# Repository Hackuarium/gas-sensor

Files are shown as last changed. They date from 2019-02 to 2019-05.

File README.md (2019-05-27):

# gas-sensor

<p align="center">
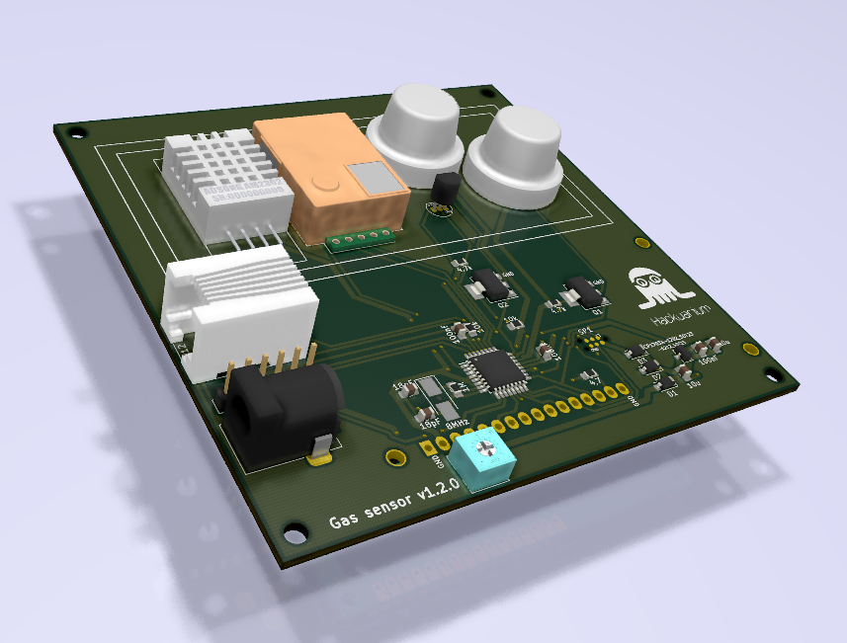
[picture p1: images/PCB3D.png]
  
</p>

The goal is to create a box allowing the determination of the gas composition of a bioreactor. The sensor that will be available are: CO2 (MH-Z19), H2 (MQ-8) and methane (MQ-4) as well as temperature (DS18B20) and humidity (DHT-22).

The board will be compatible with arduino Lilapad Pro using a dedicated PCB.

Need to compensate for humidity and temperature ???

- https://forum.arduino.cc/index.php?topic=433045.0

## Cloning the project

This project uses SUBMODULES

In order to clone use:

`git clone --recurse-submodules https://github.com/hackuarium/gas-sensor`

To update the submodules

`git submodule update --recursive --remote`

## Sensors

| name_pin | function    | model   |                             | Arduino library                                |
| -------- | ----------- | ------- | --------------------------- | ---------------------------------------------- |
| CH4      | CH4         | MQ-4    |                             |                                                |
| H2       | H2          | MQ-8    |                             |                                                |
| CO2      | CO2         | MH-Z19  | 3.3v (for RX / TX) + 5v!!!! | https://github.com/crisap94/MHZ19              |
| TEMP     | temperature | DS18B20 |                             |                                                |
| HUM      | humidity    | DHT-22  |                             | https://github.com/adafruit/DHT-sensor-library |

Gaz sensor: http://www.china-total.com/Product/meter/gas-sensor/Gas-sensor.htm

Gaz sensor on sparkfun:
https://www.sparkfun.com/products/8891
https://www.sparkfun.com/products/9404

Gaz sensor on mysensors: https://www.mysensors.org/build/gas

Drying the air / pumping
Particulate or Coalescing Filters
http://www.pneumaticplus.com/pneumaticplus-saf4000-series-particulate-air-filter-1-2-npt-with-bracket/
https://www.aliexpress.com/item/15L-M-12V-dc-electric-diaphragm-brush-small-air-compressor-pump/1790013118.html

Fans

https://www.pelonistechnologies.com/micro-fans

Pneumatic
https://www.alibaba.com/product-detail/A102-China-sup

## Pinout

| n° Arduino | port | pin      |                  |     |
| ---------- | ---- | -------- | ---------------- | --- |
| A0         | PC0  | A0       | H2               |     |
| A1         | PC1  | A1       | H2_ON            |     |
| A2         | PC2  | A2       | CO2_RX           |     |
| A3         | PC3  | A3       | CO2_TX           |     |
| A4         | PC4  | SDA      | Slave I2C        |     |
| A5         | PC5  | SCL      | Slave I2C        |     |
| A6         | ADC6 | A6       | CH4              |     |
| A7         | ADC7 | A7       | CH4_ON           |     |
| 0          | PD0  | RX       | FTDI             |     |
| 1          | PD1  | TX       | FTDI             |     |
| 2          | PD2  | D2       | /                |     |
| 3          | PD3  | D3       | PWM_MH-Z19       | PWM |
| 4          | PD4  | D4       | TEMPERATURE      |     |
| 5          | PD5  | D5       | HUMIDITY         | PWM |
| 6          | PD6  | D6       | LCD RS           | PWM |
| 7          | PD7  | D7       | /                |     |
| 8          | PB0  | D8       | LCD E            |     |
| 9          | PB1  | D9       | LCD LED          | PWM |
| 10         | PB2  | D10      | LCD1             | PWM |
| 11         | PB3  | MOSI D11 | LCD2             | PWM | mh |
| 12         | PB4  | MISO D12 | LCD3             |     |
| 13         | PB5  | SCK D13  | LCD4             |     |

n.b: Two pins (PD2 and PD7) are free and could be used to add a fourth sensor.

## Power supply

- plug for 5V
- MCP1703-33 for µC power supply

## Schematic
Here is the schematic of the main components of the project:

ATMega328P:
<p align="center">
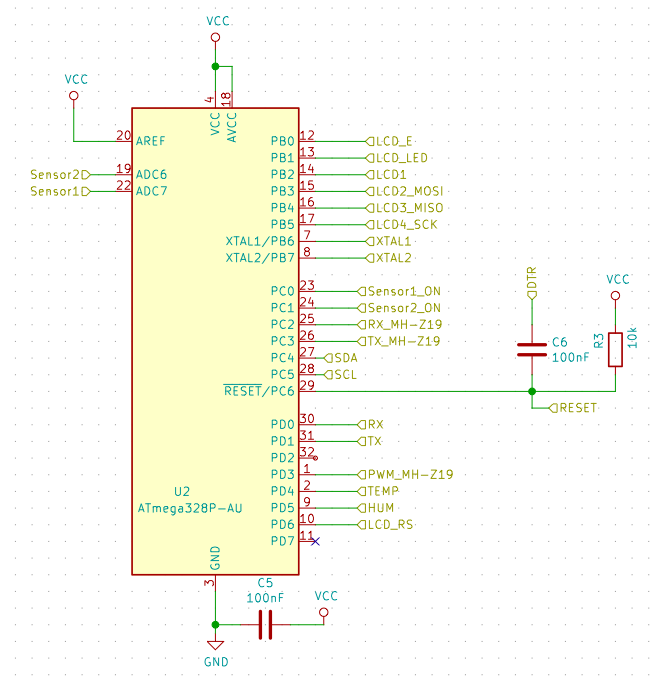
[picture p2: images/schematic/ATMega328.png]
  
</p>
Sensors:
<p align="center">
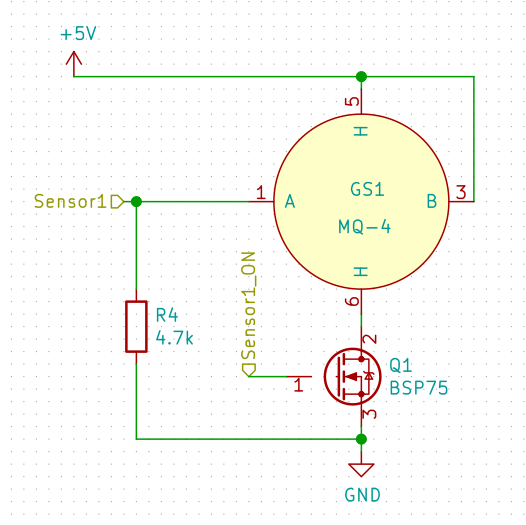
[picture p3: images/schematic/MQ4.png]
  
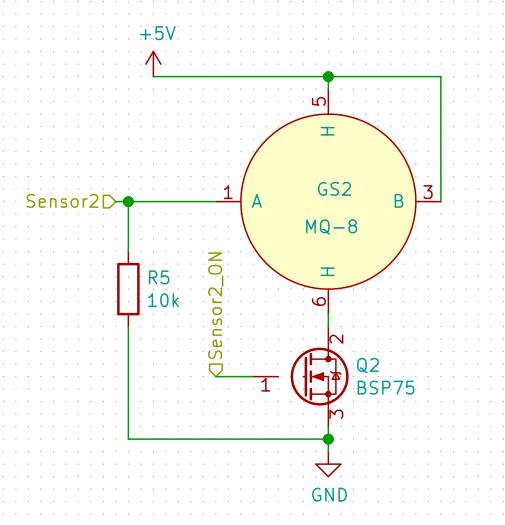
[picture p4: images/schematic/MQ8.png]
  
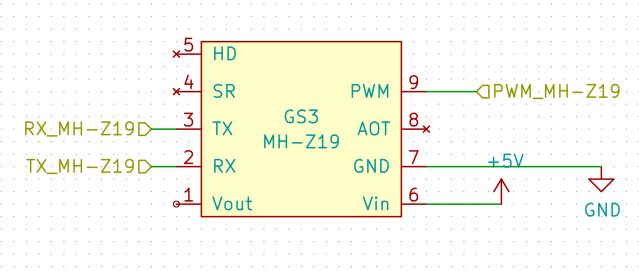
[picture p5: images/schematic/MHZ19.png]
  
</p>
<p align="center">
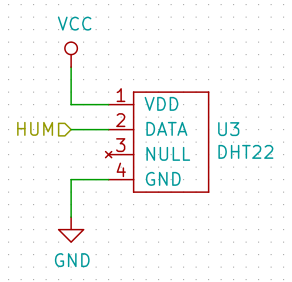
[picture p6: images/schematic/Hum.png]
  
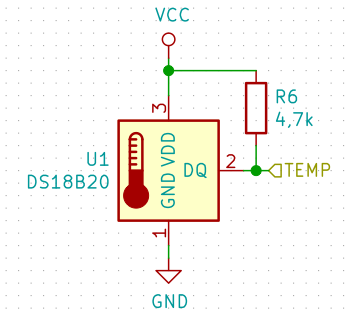
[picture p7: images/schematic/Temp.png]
  
</p>
Others (LCD, crystal and voltage regulator):
<p align="center">
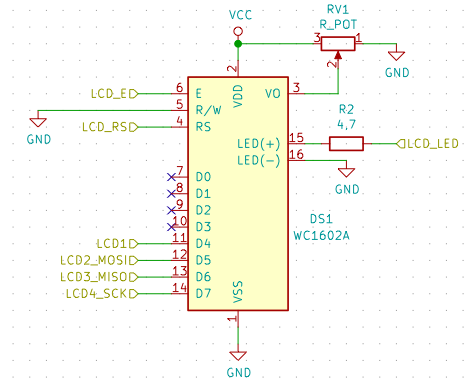
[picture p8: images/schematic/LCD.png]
  
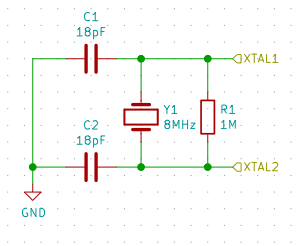
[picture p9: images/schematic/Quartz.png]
  
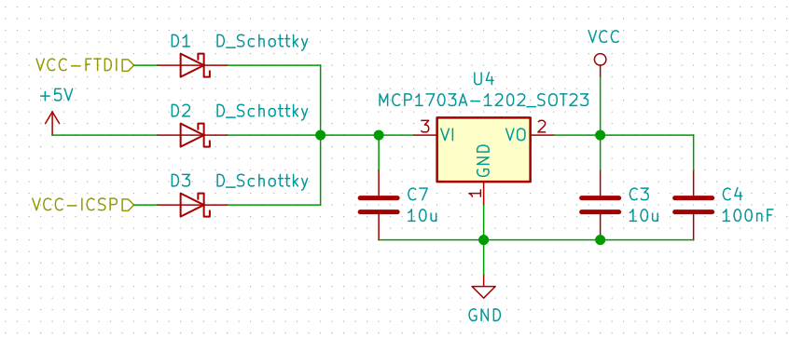
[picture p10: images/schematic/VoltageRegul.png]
  
</p>

## List of components
| Type           | Value | Quantity | Footprint                   |
|----------------|-------|----------|-----------------------------|
| Resistor       | 1M    | 1        | 0805 Handsolder             |
| Resistor       | 10k   | 2        | 0805 Handsolder             |
| Resistor       | 4.7k  | 2        | 0805 Handsolder             |
| Resistor       | 4.7   | 1        | 0805 Handsolder             |
| Potentiometer  |       | 1        | TRIM_3362R-1-222            |
| Capacitor      | 10µF  | 2        | 0805 Handsolder             |
| Capacitor      | 100nF | 3        | 0805 Handsolder             |
| Capacitor      | 18pF  | 2        | 0805 Handsolder             |
| Diode Shottky  |       | 3        | D_SOD-123                   |
| BSP75          |       | 2        | SOT-223-3_TabPin3           |
| Crystal        | 8Mhz  | 1        | Crystal_SMD_5032 Handsolder |
| MCP-1703A      |       | 1        | SOT-23                      |
| ATMega328P-AU  |       | 1        | TQFP-32_7x7mm_P0.8mm        |
| 5V power source|       | 1        | BarrelJack_Horizontal       |
| RJ12           |       | 1        | RJ12_Amphenol_54601         |
| LCD Screen     |       | 1        | WC1602A                     |
| MHZ-19 (CO2)   |       | 1        | footprints: MHZ-19          |
| MQ-4 (CH4)     |       | 1        | footprints: MQ-4            |
| MQ-8 (H2)      |       | 1        | footprints: MQ-8            |
| DHT22 (Hum)    |       | 1        | footprints: DHT-22_HOR      |
| DS18B20 (Temp) |       | 1        | TO-92_Inline                |

## Inspiration for PCB

* https://github.com/Hackuarium/esp-12e/tree/master/kicad

  - ICSP - TAG connect - take care of pin mapping !
  - RJ12 - 6P6C
  - FTDI232
  - LCD: WC1602A

## Get inspired from scale board

- https://github.com/Hackuarium/beemos/tree/master/scale-i2c/eagle
- https://github.com/Hackuarium/esp-12e/tree/master/kicad/libs

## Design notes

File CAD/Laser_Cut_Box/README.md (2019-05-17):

The case is designed to be cut in a 3mm-wide material, using a CNC (Computer Numerical Control) router, mounted with a 1,2mm-drill bit. Plexiglas has been used and shows relative good performances. Before cutting, drilling parameters must be set as follow:
* the outer contour of each piece must be set at "outside cut".
* all the other "holes" must be set at "inside cut"

Here are some pictures of the mounted box, without the hermetic "aquarium" in the middle.
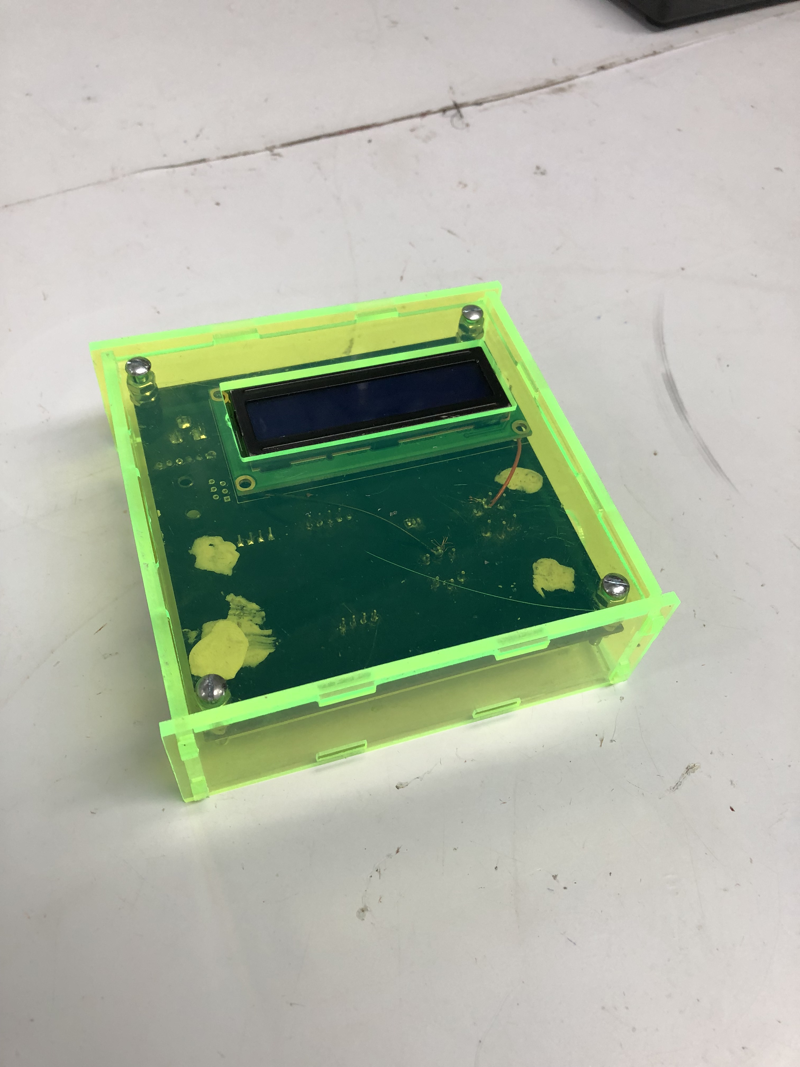
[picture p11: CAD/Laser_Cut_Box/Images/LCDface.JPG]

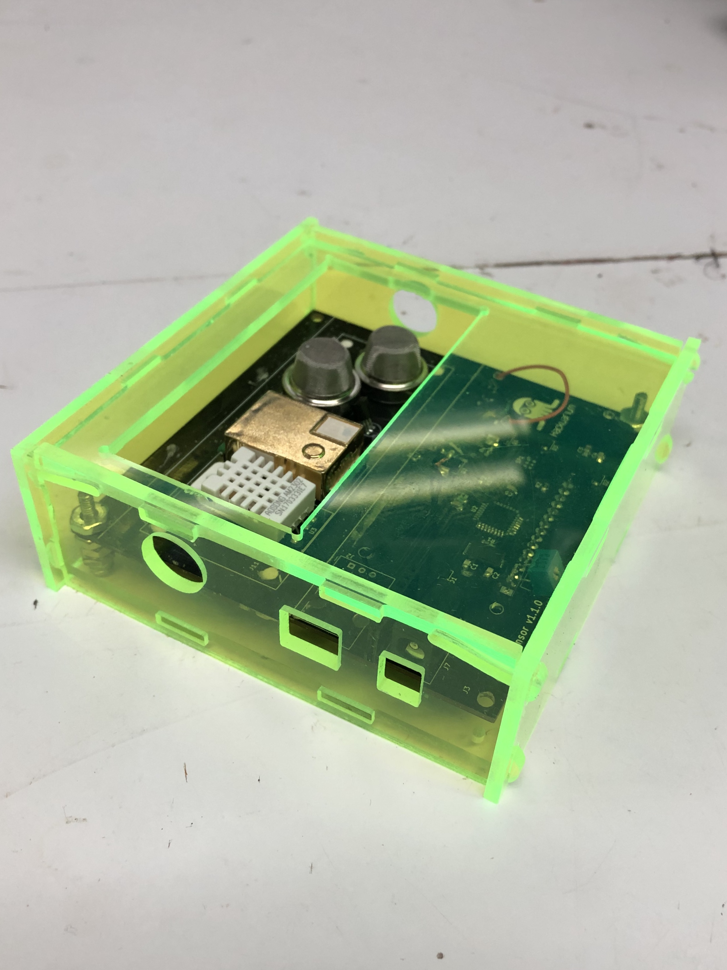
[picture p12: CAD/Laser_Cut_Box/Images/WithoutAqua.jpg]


When all the pieces are correctly obtained, one can easily assemble the case proceeding as follow:
* Glue the different parts of the aquarium together. Acrylic resine Veracril© has been used.
* Then, glue the plexiglas box directly on the chip. Assure that it is well hermetic. Silicon gun was used for ensuring absence of leaks.
* Screw the chip with the "bottom" part (the one having a round hole in each corner) using M3 screws. One can use bolts for instance to adjsut the height, as seen in the picture:
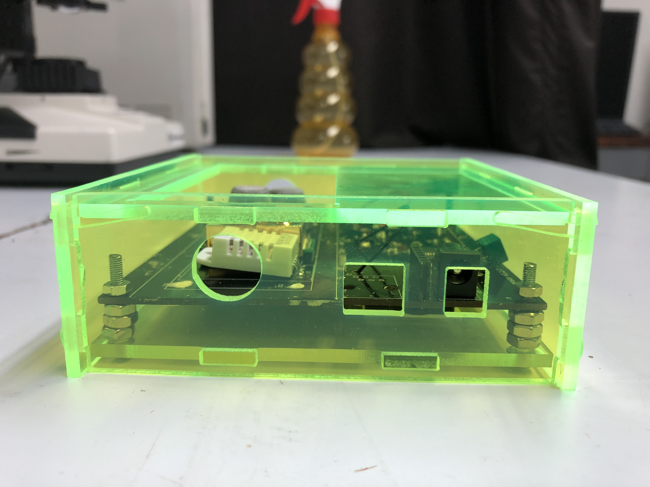
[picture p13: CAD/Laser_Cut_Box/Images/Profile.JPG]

* Place both the "left" and "right" part (the ones with the linear split and the hole for the gas pipe) on each side of the chip.
* Slide the "top" part above it and between the "left" and "right" parts.
* Clip the "up" and "down" parts to the case.

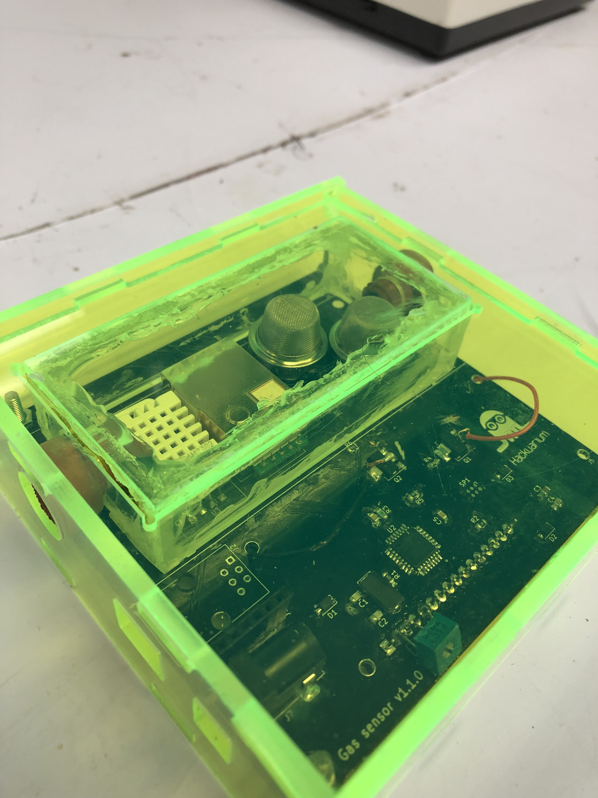
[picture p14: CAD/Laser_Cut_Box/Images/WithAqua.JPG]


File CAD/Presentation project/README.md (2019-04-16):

This folder contains temporary designs that were solely used for a presentation showing current progress on the project.

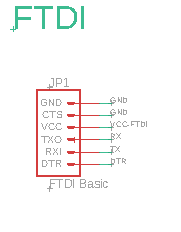
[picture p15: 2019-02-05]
images/ftdi.png

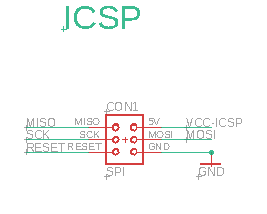
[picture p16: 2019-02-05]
images/icsp.png

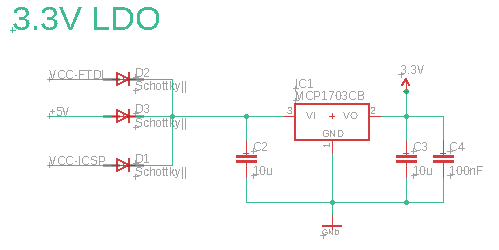
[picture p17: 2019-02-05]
images/ldo.png

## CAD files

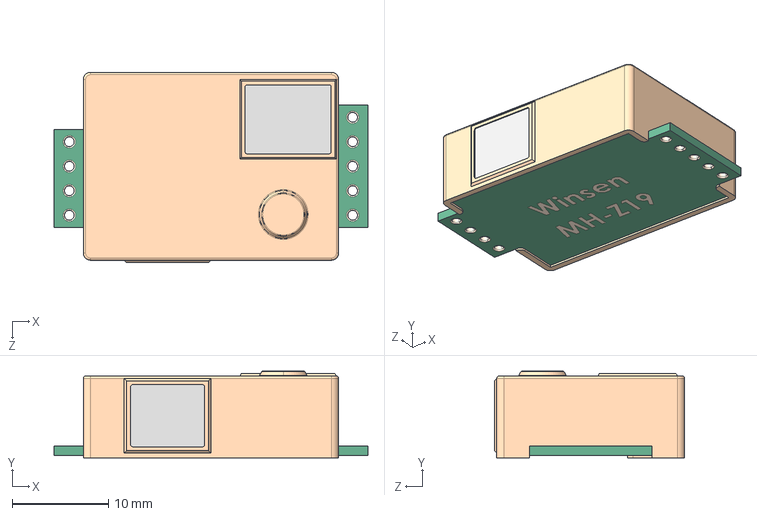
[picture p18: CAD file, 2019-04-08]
kicad/shapes3D/MH-Z19.STEP
32.6 x 9.00 x 19.7 mm

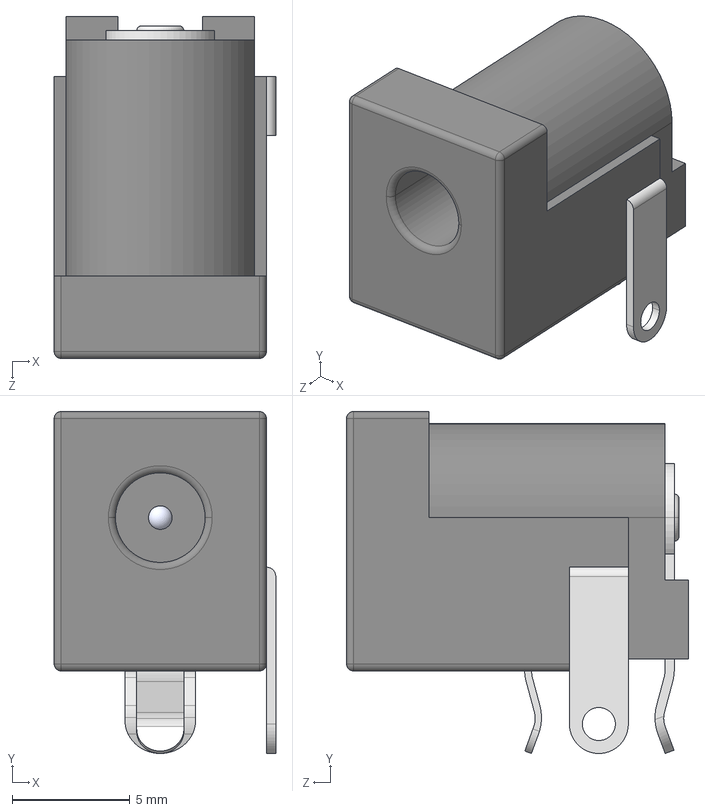
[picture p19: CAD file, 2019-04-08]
kicad/shapes3D/CUI_PJ-017C.step
9.40 x 14.5 x 14.5 mm

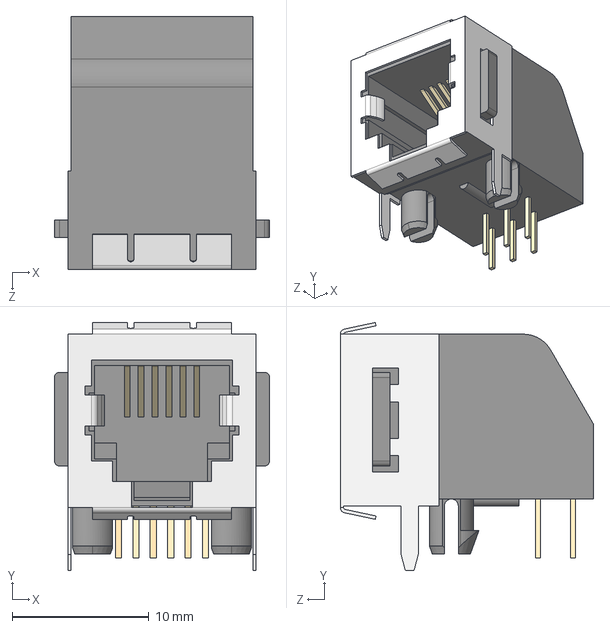
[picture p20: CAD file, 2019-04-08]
kicad/shapes3D/rj12_90deg.step
15.7 x 18.1 x 18.5 mm

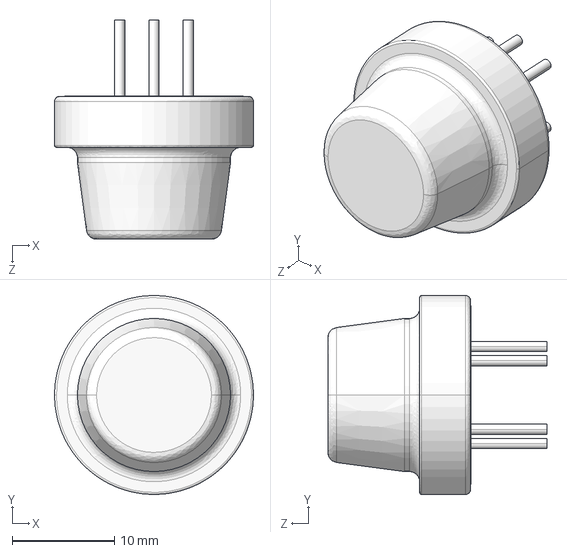
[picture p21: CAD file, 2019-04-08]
kicad/shapes3D/MQ135.STEP
19.5 x 19.5 x 21.5 mm

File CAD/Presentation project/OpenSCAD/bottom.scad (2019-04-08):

$fn = 50;

bottom();

//The bottom part (with LCD screen)
module bottom(bLength = 106, bWidth = 106, bHeight = 11, bWalls = 3, DiamScrew = 3){
    difference(){
        cube([bLength, bWidth, bHeight], center = true);
        translate([0,0,1.501]){
            cube([bLength-2*bWalls, bWidth-2*bWalls, bHeight-bWalls], center = true);
        }
        
        //hole for the screen
        screen_L = 70.7;
        screen_W = 23.8;
        X_POS = screen_L/2+4.2;
        Y_POS = screen_W/2+12.85;
        translate([-bLength/2+bWalls+X_POS,bWidth/2-bWalls-Y_POS,-3]) cube([screen_L, screen_W, 2*bWalls],center = true);
        //holes for the screw
        OFFSET = 3.4;
        translate([(bLength-2*bWalls)/2-OFFSET,(bWidth-2*bWalls)/2-OFFSET,-bWalls])Screwhole(DiamScrew, bWalls);
        translate([-(bLength-2*bWalls)/2+OFFSET,(bWidth-2*bWalls)/2-OFFSET,-bWalls])Screwhole(DiamScrew, bWalls);
        translate([-(bLength-2*bWalls)/2+OFFSET,-(bWidth-2*bWalls)/2+OFFSET,-bWalls])Screwhole(DiamScrew, bWalls);
        translate([(bLength-2*bWalls)/2-OFFSET,-(bWidth-2*bWalls)/2+OFFSET,-bWalls])Screwhole(DiamScrew, bWalls);
    }
        
}

module Screwhole(DiamScrew = 3, bWalls = 3){
    cylinder(d=DiamScrew, h=2*bWalls, center = true);
}

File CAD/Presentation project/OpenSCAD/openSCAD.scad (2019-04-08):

$fn = 50;

use <top.scad>
use <bottom.scad>
use <plexiBox.scad>
use <pcb.scad>

openSCAD();

//Dimensions for top box:
tLength = 106;
tWidth = 106;
tHeight = 23;
tWalls = 3;

//Dimensions for bottom box
bLength = 106;
bWidth = 106;
bHeight = 11;
bWalls = 3;

//Dimensions for plexibox
pLength = 100;
pWidth = 46.35;
pHeight = 23;
pWalls = 6;

//Dimensions for PCB
pcbL = 100;
pcbW = 100;
pcbH = 1;

//Dimensions for screw
DiamScrew = 3;

//Dimensions for pipe
radPipe = 6;

module openSCAD(){
    top(tLength, tWidth, tHeight, tWalls, DiamScrew, pLength, pWidth, radPipe);
    translate([0,(tWidth-2*tWalls-pWidth)/2-7.15,0]){
        color("LightCyan",0.5) plexiBox(pLength, pWidth, pHeight, pWalls, radPipe, DiamScrew);
    }
    rotate([0,0,180]){
        translate([0,0,-18])bottom(bLength, bWidth, bHeight, bWalls, DiamScrew);
    }
    translate([0,0,-12]){
        //pcb(pcbL, pcbW, pcbH);
    }

}

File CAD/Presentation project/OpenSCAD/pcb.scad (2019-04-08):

$fn = 50;

pcb();

module pcb(pcbL = 100, pcbW = 100, pcbH = 1){
    color("pink") cube([pcbL,pcbW, pcbH],center = true);
}

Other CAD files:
CAD/Laser_Cut_Box/Test_Pro_Cutting.FCStd
CAD/Laser_Cut_Box/Final_Cut_Box.FCStd
CAD/Presentation project/OpenSCAD/Pipehole.scad
CAD/Presentation project/OpenSCAD/Screwhole.scad
CAD/Presentation project/OpenSCAD/plexiBox.scad
CAD/Presentation project/OpenSCAD/top.scad

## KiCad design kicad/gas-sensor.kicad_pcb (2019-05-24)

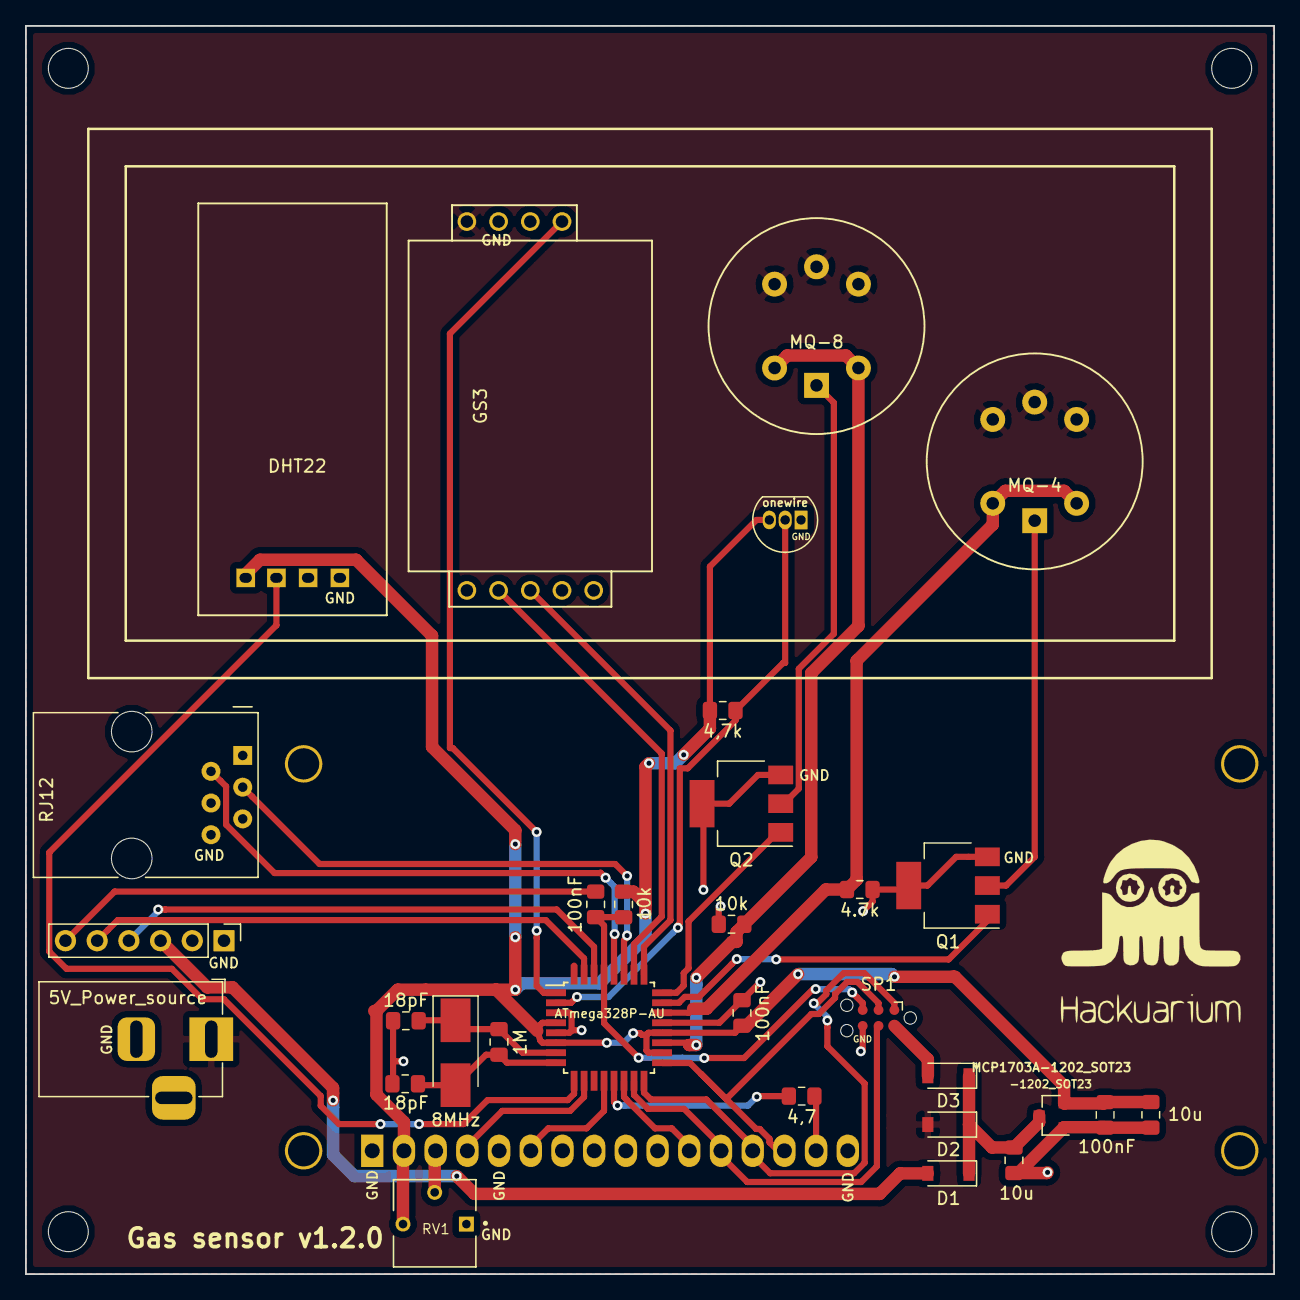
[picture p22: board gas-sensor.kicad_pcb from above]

Board: 2 copper layers, 100.0 x 100.0 mm, 37 parts (1 on the bottom side), 34 nets.

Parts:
C1, C2: 18pF; C_0805_2012Metric_Pad1.15x1.40mm_HandSolder
C3, C7: 10u; C_0805_2012Metric_Pad1.15x1.40mm_HandSolder
C4, C5, C6: 100nF; C_0805_2012Metric_Pad1.15x1.40mm_HandSolder
D1, D2, D3: D_Schottky; D_SOD-123
DS1: WC1602A
G1: LOGO; hackuarium
GS1: MQ-4
GS2: MQ-8
GS3: MH-Z19
J1: Conn FT232RL; PinHeader_1x06_P2.54mm_Vertical
J2: RJ12; RJ12_Amphenol_54601
J3, J4, J5, J6: hole; MountingHole_3.2mm_M3
J7: 5V_Power_source; BarrelJack_Horizontal
Q1, Q2: BSP75; SOT-223-3_TabPin3
R1: 1M; R_0805_2012Metric_Pad1.15x1.40mm_HandSolder
R2: 4,7; R_0805_2012Metric_Pad1.15x1.40mm_HandSolder
R3, R5: 10k; R_0805_2012Metric_Pad1.15x1.40mm_HandSolder
R4: 4.7k; R_0805_2012Metric_Pad1.15x1.40mm_HandSolder
R6: 4,7k; R_0805_2012Metric_Pad1.15x1.40mm_HandSolder
RV1: R_POT; TRIM_3362R-1-222
SP1: ICSP; Tag-Connect_TC2030-IDC-NL_2x03_P1.27mm_Vertical
U1: DS18B20; TO-92_Inline
U2: ATmega328P-AU; TQFP-32_7x7mm_P0.8mm
U3: DHT22; DHT22_HOR
U4: MCP1703A-1202_SOT23; SOT-23
Y1: 8MHz; Crystal_SMD_5032-2Pin_5.0x3.2mm_HandSoldering

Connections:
+5V: D2.2, GS1.3, GS1.4, GS1.5, GS2.3, GS2.4, GS2.5, GS3.6, J7.1
/DTR: C6.1, J1.6
/HUM: U2.9, U3.2
/LCD1: DS1.11, U2.14
/LCD2_MOSI: DS1.12, SP1.4, U2.15
/LCD3_MISO: DS1.13, SP1.1, U2.16
/LCD4_SCK: DS1.14, SP1.3, U2.17
/LCD_E: DS1.6, U2.12
/LCD_LED: R2.1, U2.13
/LCD_RS: DS1.4, U2.10
/PWM_MH-Z19: GS3.9, U2.1
/RESET: C6.2, R3.2, SP1.5, U2.29
/RX: J1.4, U2.30
/RX_MH-Z19: GS3.3, U2.25
/SCL: J2.2, U2.28
/SDA: J2.3, U2.27
/Sensor1: GS1.1, GS1.2, R4.1, U2.22
/Sensor1_ON: Q1.1, U2.23
/Sensor2: GS2.1, GS2.2, R5.1, U2.19
/Sensor2_ON: Q2.1, U2.24
/TEMP: R6.2, U1.2, U2.2
/TX: J1.5, U2.31
/TX_MH-Z19: GS3.2, U2.26
/VCC-FTDI: D1.2, J1.3
/VCC-ICSP: D3.2, SP1.2
/XTAL1: C1.1, R1.1, U2.7, Y1.1
/XTAL2: C2.1, R1.2, U2.8, Y1.2
GND: C1.2, C2.2, C3.2, C4.2, C5.2, C7.2, DS1.1, DS1.5, DS1.16, GS3.7, J1.1, J2.4, J2.6, J7.2, Q1.3, Q2.3, R4.2, R5.2, RV1.1, SP1.6, U1.1, U2.3, U2.5, U2.21, U3.4, U4.1
unnamed: C7.1, D1.1, D2.1, D3.1, U4.3
unnamed: DS1.3, RV1.2
unnamed: DS1.15, R2.2
unnamed: GS1.6, Q1.2
unnamed: GS2.6, Q2.2
VCC: C3.1, C4.1, C5.1, DS1.2, R3.1, R6.1, RV1.3, U1.3, U2.4, U2.6, U2.18, U2.20, U3.1, U4.2

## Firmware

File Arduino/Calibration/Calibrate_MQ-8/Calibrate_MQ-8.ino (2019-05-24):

/*Calibration of the sensor MQ-8, and allow to test it afterwards*/
// inspiration: http://sandboxelectronics.com/?p=196

/************************Hardware Related Macros************************************/
#define         H2_PIN                       A6     //define which analog input channel you are going to use
#define         H2_ON_PIN                    A1     // set on HIGH to turn the sensor on
#define         RL_VALUE                     10     //define the load resistance on the board, in kilo ohms
#define         RO_CLEAN_AIR_FACTOR          70     //RO_CLEAR_AIR_FACTOR=(Sensor resistance in clean air)/RO,
                                                     //derived from the chart in datasheet
 
/***********************Software Related Macros************************************/
#define         CALIBRATION_SAMPLE_TIMES     300    //define how many samples you are going to take in the calibration phase
#define         CALIBRATION_SAMPLE_INTERVAL  500    //define the time interal(in milisecond) between each samples in the
                                                    //cablibration phase
#define         READ_SAMPLE_INTERVAL         100    //define how many samples you are going to take in normal operation
#define         READ_SAMPLE_TIMES            20     //define the time interal(in milisecond) between each samples in 
                                                    //normal operation
                                                     
/*****************************Globals***********************************************/
float           H2Curve[2]  =  {-1.44, 4.25};       //Line representing the relationship between the log of the concentration
                                                    //of H2 in ppm (x) and the log of the ratio of resistances Rs/Ro (y)
                                                    //{a, b}, log(y) = a*log(x) + b;
                                                    //The two points chosen: {200, 8.5} and {10000, 0.403}  
 
float           Ro           =  14.01;              //Last Ro found with this programm, 14.01 kOhm. TOCHANGE at evry new calibration
bool            Calib_bool   =  true;              //Set to True if calibration is needed (fresh air condition expected)


void setup() {
  Serial.begin(9600);                               //UART setup, baudrate = 9600bps
  pinMode(H2_ON_PIN, OUTPUT);
  digitalWrite(H2_ON_PIN, HIGH);
  if(Calib_bool){
    Serial.print("Calibrating...\n");                
    Ro = MQCalibration();                           //Calibrating the sensor. Please make sure the sensor is in clean air
                                                    //when you perform the calibration 
    Serial.println("Calibration is done: Ro = " + String(Ro) + " kOhm");
  }                                                                     

}

//Average the value read from the analog pin, and if in the range, compute the ppm from it
void loop(){
  int i;
  float sensorValue=0;
  float analog;
 
  while(true){
    for (i = 0; i < READ_SAMPLE_TIMES; i++){
      analog = analogRead(H2_PIN);
      Serial.println("analog = " + String(analog) + " / "); 
      sensorValue += analog;
      delay(READ_SAMPLE_INTERVAL);
    }
    
    sensorValue = sensorValue/READ_SAMPLE_TIMES;
    if(sensorValue <= 1){
      Serial.println("Not enough H2 (" + String(sensorValue) + ")");
    }
    else if(sensorValue >= 1023){
      Serial.println("Too much H2 (" + String(sensorValue) + ")");
    }
    else{
    Serial.print("Value = " + String(sensorValue) + " / ");
    getH2(sensorValue);
    }
    sensorValue = 0;
    delay(1000);
  }
}

/***************************** MQCalibration ****************************************
Input:   mq_pin - analog channel
Output:  Ro of the sensor
Remarks: This function assumes that the sensor is in clean air. It use  
         MQResistanceCalculation to calculates the sensor resistance in clean air 
         and then divides it with RO_CLEAN_AIR_FACTOR.
************************************************************************************/ 
float MQCalibration() {
  int i;
  float val=0;
  delay(5000);
  for (i=0;i<CALIBRATION_SAMPLE_TIMES;i++) {            //take multiple samples
    int pin_value = analogRead(H2_PIN);
    if(i%5 == 0){
      Serial.println("sample n°:"+ String(i) + ", pin value = " + String(pin_value));
    }
    val += MQResistanceCalculation(pin_value);
    delay(CALIBRATION_SAMPLE_INTERVAL);
  }
  val = val/CALIBRATION_SAMPLE_TIMES;                   //calculate the average value
 
  val = val/RO_CLEAN_AIR_FACTOR;                        //divided by RO_CLEAN_AIR_FACTOR yields the Ro 
                                                       //according to the chart in the datasheet 
                                                         
  return val; 
}

/*****************************  getH2 *********************************************3
Input:   /
Output:  Concentration of H2 in ppm
Remarks: This function gets the concentration of H2 from the average of the values
          read on the analog pin.
************************************************************************************/ 
void getH2(float sensorValue){
  
  long H2ppm;
  H2ppm = MQGetPercentage(MQResistanceCalculation(sensorValue)/Ro,H2Curve);
  Serial.println("H2ppm = " + String(H2ppm) + "ppm");
}
 
/****************** MQResistanceCalculation ****************************************
Input:   raw_adc - raw value read from adc, which represents the voltage
Output:  the calculated sensor resistance Rs
Remarks: The sensor and the load resistor forms a voltage divider. Given the voltage
         across the load resistor and its resistance, the resistance of the sensor
         could be derived.
************************************************************************************/ 
float MQResistanceCalculation(float raw_adc) {
  return (float)RL_VALUE*(1023-raw_adc)/raw_adc;
}
 
/*****************************  MQGetPercentage **********************************
Input:   rs_ro_ratio - Rs divided by Ro
         pcurve      - pointer to the curve of the target gas
Output:  ppm of the target gas
Remarks: By using the slope and a point of the line. The x(logarithmic value of ppm) 
         of the line could be derived if y(rs_ro_ratio) is provided. As it is a 
         logarithmic coordinate, power of 10 is used to convert the result to non-logarithmic 
         value.
************************************************************************************/ 
long  MQGetPercentage(float rs_ro_ratio, float *pcurve) {
  return pow(10, (log(rs_ro_ratio)-pcurve[1])/pcurve[0]);
}

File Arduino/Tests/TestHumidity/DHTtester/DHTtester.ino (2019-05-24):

// Example testing sketch for various DHT humidity/temperature sensors
// Written by ladyada, public domain

// REQUIRES the following Arduino libraries:
// - DHT Sensor Library: https://github.com/adafruit/DHT-sensor-library
// - Adafruit Unified Sensor Lib: https://github.com/adafruit/Adafruit_Sensor

#include "DHT.h"

#define DHT_PIN 5     // Digital pin connected to the DHT sensor
// Feather HUZZAH ESP8266 note: use pins 3, 4, 5, 12, 13 or 14 --
// Pin 15 can work but DHT must be disconnected during program upload.

// Uncomment whatever type you're using!
//#define DHTTYPE DHT11   // DHT 11
#define DHTTYPE DHT22   // DHT 22  (AM2302), AM2321
//#define DHTTYPE DHT21   // DHT 21 (AM2301)

// Connect pin 1 (on the left) of the sensor to +5V
// NOTE: If using a board with 3.3V logic like an Arduino Due connect pin 1
// to 3.3V instead of 5V!
// Connect pin 2 of the sensor to whatever your DHTPIN is
// Connect pin 4 (on the right) of the sensor to GROUND
// Connect a 10K resistor from pin 2 (data) to pin 1 (power) of the sensor

// Initialize DHT sensor.
// Note that older versions of this library took an optional third parameter to
// tweak the timings for faster processors.  This parameter is no longer needed
// as the current DHT reading algorithm adjusts itself to work on faster procs.
DHT dht(DHT_PIN, DHTTYPE);

void setup() {
  Serial.begin(9600);
  Serial.println(F("DHTxx test!"));

  dht.begin();
}

void loop() {
  // Wait a few seconds between measurements.
  delay(5000);

  // Reading temperature or humidity takes about 250 milliseconds!
  // Sensor readings may also be up to 2 seconds 'old' (its a very slow sensor)
  float h = dht.readHumidity();
  // Read temperature as Celsius (the default)
  float t = dht.readTemperature();
  // Read temperature as Fahrenheit (isFahrenheit = true)
  float f = dht.readTemperature(true);

  // Check if any reads failed and exit early (to try again).
  if (isnan(h) || isnan(t) || isnan(f)) {
    Serial.println(F("Failed to read from DHT sensor!"));
    return;
  }

  // Compute heat index in Fahrenheit (the default)
  float hif = dht.computeHeatIndex(f, h);
  // Compute heat index in Celsius (isFahreheit = false)
  float hic = dht.computeHeatIndex(t, h, false);

  Serial.print(F("Humidity: "));
  Serial.print(h);
  Serial.print(F("%  Temperature: "));
  Serial.print(t);
  Serial.print(F("°C "));
  Serial.print(f);
  Serial.print(F("°F  Heat index: "));
  Serial.print(hic);
  Serial.print(F("°C "));
  Serial.print(hif);
  Serial.println(F("°F"));
}

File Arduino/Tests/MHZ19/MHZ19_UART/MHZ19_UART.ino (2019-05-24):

// adapted from https://forum.mysensors.org/topic/6528/mh-z19-co2-sensor/14
//Show ppm of CO2 using UART
#include <SoftwareSerial.h>

#define RX    A2
#define TX    A3

unsigned long co2MeasurementInterval = 10000;     // Time to wait between reads (in milliseconds).
SoftwareSerial co2Serial(A2, A3);                    // RX, TX . You can choose other pins if you prefer. Remember: TX (transmit) on the sensor must be connected to RX (receive) on the Arduino.

void setup() 
{
  delay(1000);
  pinMode(RX, INPUT);
  pinMode(TX, OUTPUT);
  Serial.begin(9600);
  delay(1000);
  co2Serial.begin(9600);
  delay(2000);
  while (co2Serial.read()!=-1) {};  //clear Co2 buffer.
  Serial.println("hello world, I am a sensor.");
  byte ABCoff[9] = {0xFF, 0x01, 0x79, 0x00, 0x00, 0x00, 0x00, 0x00, 0x80};
  co2Serial.write(ABCoff, 9); //desactivate automatic calibration every 24h 
}

void loop() 
{
  // You should not change this variable:
  static unsigned long previousCo2Millis = 0;       // Used to remember the time of the last temperature measurement.

  unsigned long currentMillis = millis();           // The time since the sensor started, counted in milliseconds. This script tries to avoid using the Sleep function, so that it could at the same time be a MySensors repeater.

  if (currentMillis - previousCo2Millis >= co2MeasurementInterval) { // this only gets triggered when enough time has passed.
    previousCo2Millis = currentMillis;
    
    long co2ppm = readCO2();    
    Serial.println("Co2 - PPM = " + String(co2ppm)); 
    Serial.print("Co2 - zzzzZZZZzzzzZZZZzzzz\n");
  }
}

// Main function that gets the Co2 data
int readCO2()
{
  while (co2Serial.read()!=-1) {};  //clear serial buffer  
  Serial.println("CO2 - Sending data request to sensor.");
  
  byte cmd[9] = {0xFF, 0x01, 0x86, 0x00, 0x00, 0x00, 0x00, 0x00, 0x79};
  byte response[9]; // for answer
  
  // command to ask for data
  co2Serial.write(cmd, 9); //request PPM CO2 

  memset(response, 0, 9); //clear the buffer

  int i = 0;
  while (co2Serial.available() == 0) {
    Serial.print("Waiting for response ");
    Serial.print(i);
    Serial.println(" s");
    delay(1000);
    i++;
  }
  if (co2Serial.available() > 0) {
      co2Serial.readBytes(response, 9);
  }

  //print out the response in hexa
  for (int j = 0; j < 9; j++){ 
    Serial.print(String(response[j], HEX));
    Serial.print(" - ");
  }
  Serial.println("END");  

  if (byte(response[0]) != 0xFF)
  {
    Serial.println("Wrong starting byte from co2 sensor! (should be FF)");
    return -1;
  }

  if (byte(response[1]) != 0x86)
  {
    Serial.println("Wrong command from co2 sensor! (should be 86)");
    return -1;
  }

  int responseHigh = (int) byte(response[2]);
  int responseLow = (int) byte(response[3]);
  int ppm = (256 * responseHigh) + responseLow;
  
  return ppm;
}

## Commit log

2018-12-04 add specdtro
    [gas-sensor.brd, gas-sensor.sch, simple-spectro.brd, simple-spectro.sch]
2019-02-05 description of new project
    [gas-sensor.brd, gas-sensor.sch]
2019-02-05 update CO2 gas sensor and reset
2019-02-05 add link to gas sensor
2019-02-05 add remarks about temperature
2019-02-13 Add Olivier file
    First draft of shematic
    [gas-sensor.kicad_pcb, gas-sensor.sch]
2019-02-26 Footprints and first PCB draft
    add kicad (+libs) and docs file, sorted libs, footprints of sensors, first draft of PCB
    [gas-sensor.kicad_pcb, gas-sensor.sch]
2019-02-26 minor changes
    [gas-sensor.kicad_pcb]
2019-03-05 First version of PCB
    with 3D components
    [gas-sensor.kicad_pcb, gas-sensor.sch]
2019-03-07 Update README.md
    change PIN configuration
2019-03-14 add gerber files and version
    [gas-sensor-B.Cu.gbr, gas-sensor-B.Mask.gbr, gas-sensor-B.Paste.gbr, gas-sensor-B.SilkS.gbr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]
2019-03-14 update pcb and submit gerber
    [gas-sensor.kicad_pcb]
2019-03-22 Update after debugging
    [Case_FreeCAD.FCStd, gas-sensor.kicad_pcb, gas-sensor.sch]
2019-03-25 gerver v1.1.0
    [gas-sensor-B.Cu.gbr, gas-sensor-B.Mask.gbr, gas-sensor-B.Paste.gbr, gas-sensor-B.SilkS.gbr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]
2019-03-26 add missing dri files in gerber.110
    [gas-sensor-B.Cu.gbr, gas-sensor-B.Mask.gbr, gas-sensor-B.Paste.gbr, gas-sensor-B.SilkS.gbr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]
2019-04-08 Rx/Tx + Potentiometer ok
    [2d-box-spectro copie.fcstd, CUI_PJ-017C.step, Case_FreeCAD.FCStd, DHT22_HOR.stp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]
2019-04-10 Update
    Plans for laser cut (simple & with clips)
    [2d-box-spectro copie.fcstd, Case_FreeCAD.FCStd, Laser_Cut_Clips.FCStd, Simple_Laser_Cut.FCStd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]
2019-04-10 Delete eagle file
    Unused and useless
    [gas-sensor.brd, gas-sensor.sch, simple-spectro.brd, simple-spectro.sch]
2019-04-10 Added voltage regulator
    [Laser_Cut_Clips.FCStd, Laser_Cut_Simple.FCStd, Pipehole.scad, Screwhole.scad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]
2019-04-22 Update CAD
    [Laser_Cut_Clips.FCStd, Laser_Cut_Clips_2.FCStd, gas-sensor.kicad_pcb, gas-sensor.sch]
2019-04-30 Update PCB
    ready for GERBER
2019-05-17 Final version of box
    [Final_Cut_Box.FCStd, Laser_Cut_Clips_V1.FCStd, Laser_Cut_Clips_V1_3D.FCStd, Laser_Cut_Clips_V2.FCStd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]
